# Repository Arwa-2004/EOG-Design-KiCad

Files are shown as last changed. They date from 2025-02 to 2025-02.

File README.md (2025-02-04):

# EOG-Design-KiCad

## Table of Contents
1. [Introduction](#introduction)
2. [Components](#components)
   - [Protection Circuit](#protection-circuit)
   - [Boost Converter](#boost-converter)
   - [5V to -5V Inverting Converter](#5v-to--5v-inverting-converter)
   - [5V to 3.3V Regulator](#5v-to-33v-regulator)
   - [Li-ion Battery Charger](#li-ion-battery-charger)
   - [EOG Filters](#eog-filters)
   - [Flash Memory, UART, and Screen](#flash-memory-uart-and-screen)
   - [ESP32-WROOM-32E](#esp32-wroom-32e)
3. [PCB Design](#pcb-design)
4. [Future Work](#future-work)
5. [Copyright](#Copyright)

## Introduction
EOG (Electrooculography) is used in medical diagnostics to assess eye health and track issues related to the retina and cornea, it is handheld as electrodes are attached. The purpose of my project is to captures eye movement signals using EOG electrodes, processes the data with an ESP32 microcontroller, and displays the results on a screen.



## Components



### Protection Circuit
Is used to ensure that the system is safe from electrical surges. I used 2A fuse to protect against short circuits and overcurrent, a reverse polarity Schottky Diode, as its name suggests it protects the circuit from damage if the power supply is connected with reverse polarity, and a TVS diode SMAJ5.0A which protects sensitive components such as ESP32 from voltage spikes.

### Boost Converter
Which boosts the voltage from +3.6V to +5V, in this case I chose TPS61252DSG. The +5V rail is used to power the filters of EOG signal.

### 5V to -5V inverting converter
I used LM2776 to provide negative -5V supply to the EOG filters.

### 5V to 3.3V regulator 
Steps down the 5V supply to 3.3V for components like the ESP32, which require a 3.3V supply.

### Li-ion Battery Charger
Which charges a single-cell Li-ion battery (3.6V–4.2V) from a 5V input like USB or external adapter.
Charger IC LTC4001EUF#PBF manages the charging process, including constant current (CC) and constant voltage (CV) phases. Moreover, protects the battery from overcharging, over-discharging, and short circuits. Example of bettery used: https://tr.farnell.com/jauch/li18650jc-26-1s1p/batt-rechargeable-li-ion-2-6ah/dp/4551054



### EOG filters
As shown in the picture, I added a 3 pin connector for the electrodes (CH- and CH+) thrid one connected to ground which is behind the ear (in the bony area) as a reference https://store.upsidedownlabs.tech/product/bioamp-cable-v2/. I used instrumentation amplifier to amplify small differential signals from EOG electrodes while rejecting common-mode noise like interference from power lines 50Hz or 60Hz,or other sources.
The INA333xxDGK has a precise gain that can be set using a single external resistor, a high CMRR, and a low noise. 
I added user safety composed of TVS diodes to safeguard the user and the equipment from voltage spikes, electrostatic discharge (ESD), or reverse polarity.

Then, I connected IA to a high pass filter of 0.053Hz to process the amplified signal and remove unwanted DC low-frequency components, ensuring that only the relevant EOG signals (related to eye movements) are processed, which is connected to 50Hz notch filter to remove power line interference of 50Hz that is connected to class 1 and 2 of low pass filter, 1st class low pass filter 23.42Hz, is used to remove high-frequency noise and ensure that only the relevant EOG signals (typically in the range of 0.1 Hz to 30 Hz) are preserved. Furthermore, integrating 2nd class low-pass filter, 19.42Hz to effectively attenuates frequencies above the cutoff frequency (19.42 Hz), ensuring that high-frequency noise is removed more aggressively, which is conncted to the ESP32.

### Flash Memory, UART, and Screen
The OLED screen (AOM12864A0-1.54WW-ANO) to show EOG signals, eye movement patterns, or system parameters. The flash memory to store EOG signals for later analysis. Finally, UART to send EOG data to a computer for analysis. Note: this EOG is designed to retrieve or analyze the stored data later as needed as I'll depend on bluetooth build inside esp32 (coding) for data transfer. a BluetoothSerial used to communicate with a Bluetooth terminal app or custom software. In short I wont need a USB.



### ESP32-WROOM-32E
Is the brain of the system, since ESP32 enables communication between the EOG system and external devices,  processes the EOG signals captured by the electrodes and amplified/filtered by the analog front-end filters, displays real-time EOG data or system status on an OLED screen, and stores EOG data in flash memory or an external SD card for later analysis.



## PCB design
I used 4 layers (signal/ gnd/ power/ signal), I made sure that sensitive analog ciruits of the filters are far away from the noisy digital parts such as esp32, and I put decoupling capacitor 100 nF close to the power pins of each IC (ESP32, INA333xxDGK, filters, etc..)





## Future Work
This project is designed to retrieve and analyze stored EOG data as needed. Future improvements and planned features include:

1. **Bluetooth Data Transfer:**
   - The ESP32's built-in Bluetooth capability will be used for wireless data transfer, eliminating the need for a USB connection.
2. **Optimized Signal Processing:**
   - Further refinement of the EOG signal filters to improve noise immunity and signal accuracy.
   - Implementation of advanced signal processing algorithms (e.g., wavelet transforms) for better eye movement detection.

3. **Wireless Charging:**
   - Integration of a wireless charging module to enhance the portability and usability of the device.

4. **Mobile App Integration:**
   - Development of a mobile app to visualize EOG data in real-time and provide diagnostic insights.

## Copyright
Copyright (c) 2025 Arwa Basal
All rights reserved.

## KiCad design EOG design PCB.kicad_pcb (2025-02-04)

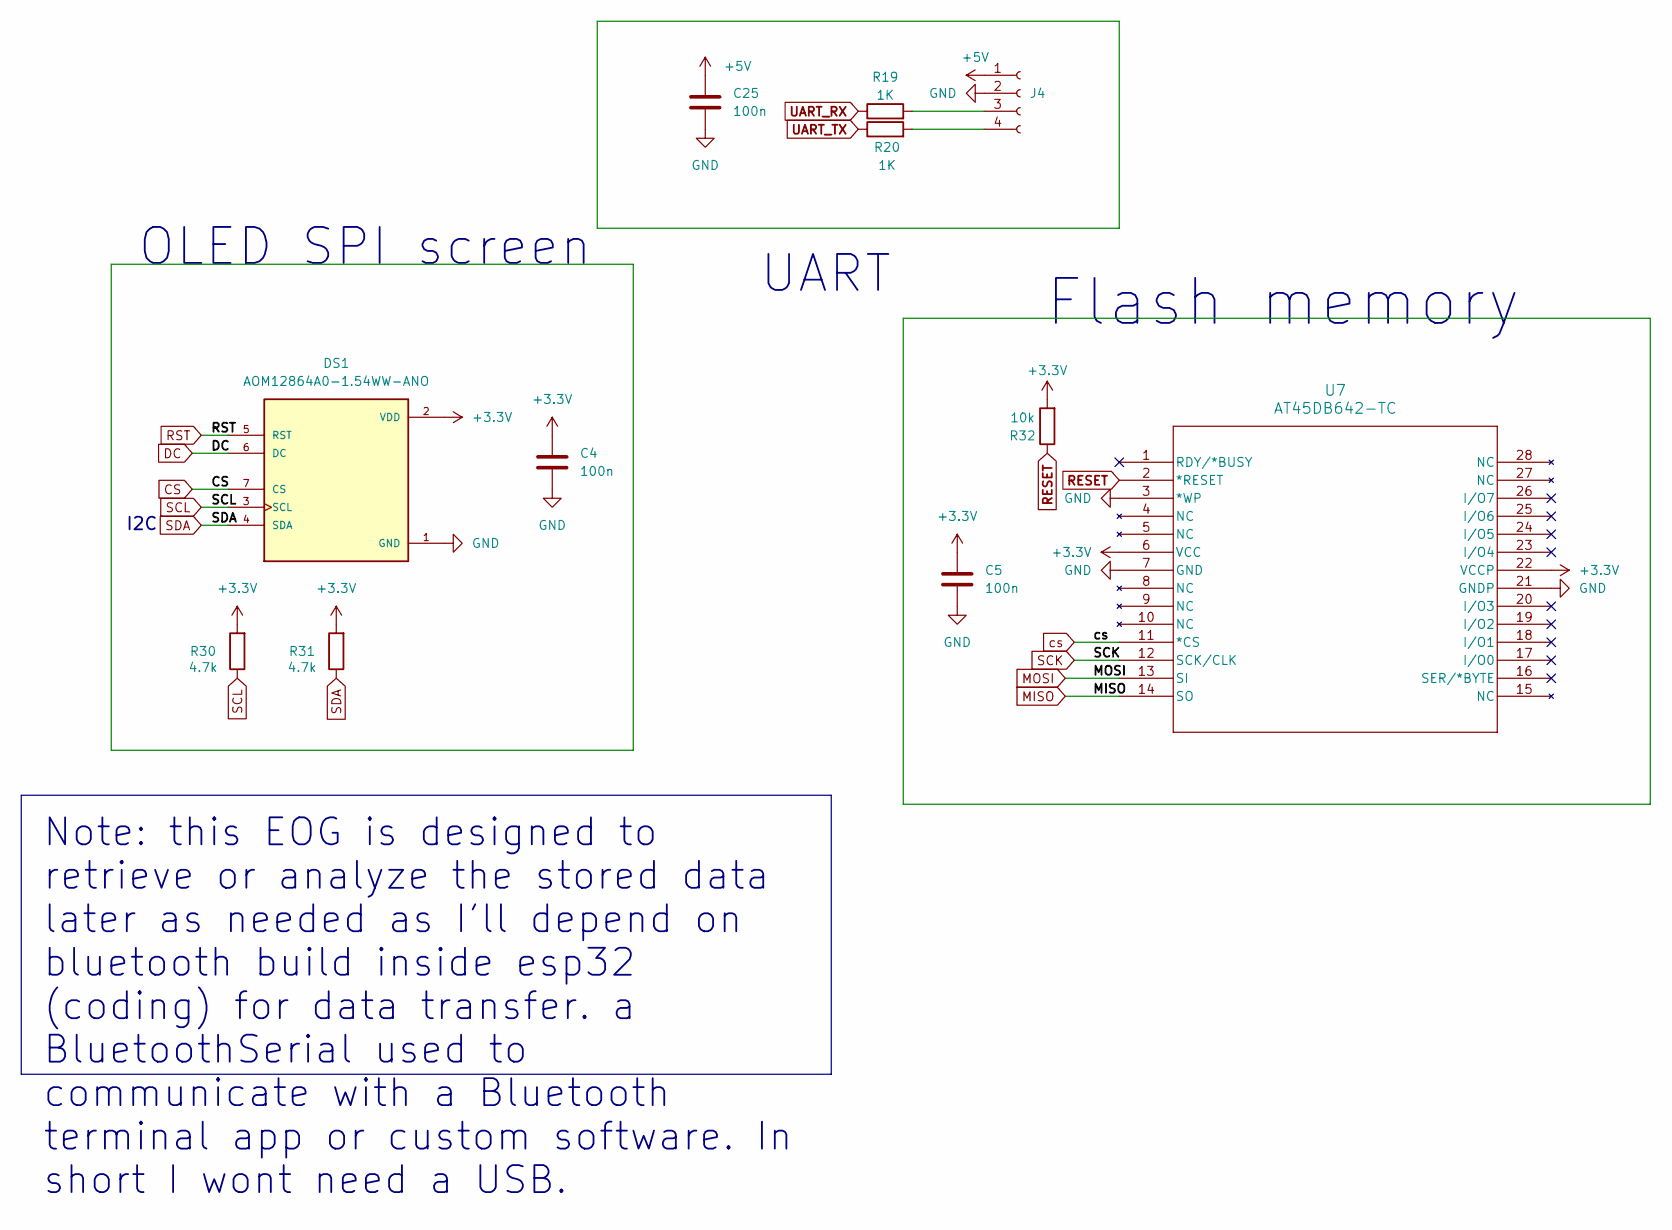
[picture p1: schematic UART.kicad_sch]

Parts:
C4, C5, C25: 100n; C_0603_1608Metric
DS1: AOM12864A0-1.54WW-ANO; LCD_AOM12864A0-1.54WW-ANO; PARTREV O; DigiKey_Part_Number 5491-AOM12864A0-1.54WW-ANO-ND
J4: Conn_01x04_Socket; PinHeader_2x02_P1.00mm_Vertical
R19, R20: 1K; R_0603_1608Metric
R30, R31: 4.7k; R_0603_1608Metric
R32: 10k; R_0603_1608Metric
U7: AT45DB642-TC; TSOP28_8x11P8_MCH

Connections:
+3.3V: C4.1, C5.1, DS1.2 (VDD), R30.2, R31.2, R32.2, U7.6 (VCC), U7.22 (VCCP); also elsewhere on the board
+5V: C25.1, J4.1; also elsewhere on the board
CS: DS1.7 (CS); also elsewhere on the board
DC: DS1.6 (DC); also elsewhere on the board
GND: C4.2, C5.2, C25.2, DS1.1 (GND), J4.2, U7.3 (*WP), U7.7 (GND), U7.21 (GNDP); also elsewhere on the board
MISO: U7.14 (SO); also elsewhere on the board
MOSI: U7.13 (SI); also elsewhere on the board
unnamed: J4.3, R19.2
unnamed: J4.4, R20.2
RESET: R32.1, U7.2 (*RESET)
RST: DS1.5 (RST); also elsewhere on the board
SCK: U7.12 (SCK/CLK); also elsewhere on the board
SCL: DS1.3 (SCL), R30.1; also elsewhere on the board
SDA: DS1.4 (SDA), R31.1; also elsewhere on the board
UART_RX: R19.1; also elsewhere on the board
UART_TX: R20.1; also elsewhere on the board
cs: U7.11 (*CS); also elsewhere on the board

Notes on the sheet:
Note: this EOG is designed to retrieve or analyze the stored data later as needed as I'll depend on bluetooth build inside esp32 (coding) for data transfer. a BluetoothSerial used to communicate with a Bluetooth terminal app or custom software. In short I wont need a USB.
OLED SPI screen
I2C
UART
Flash memory

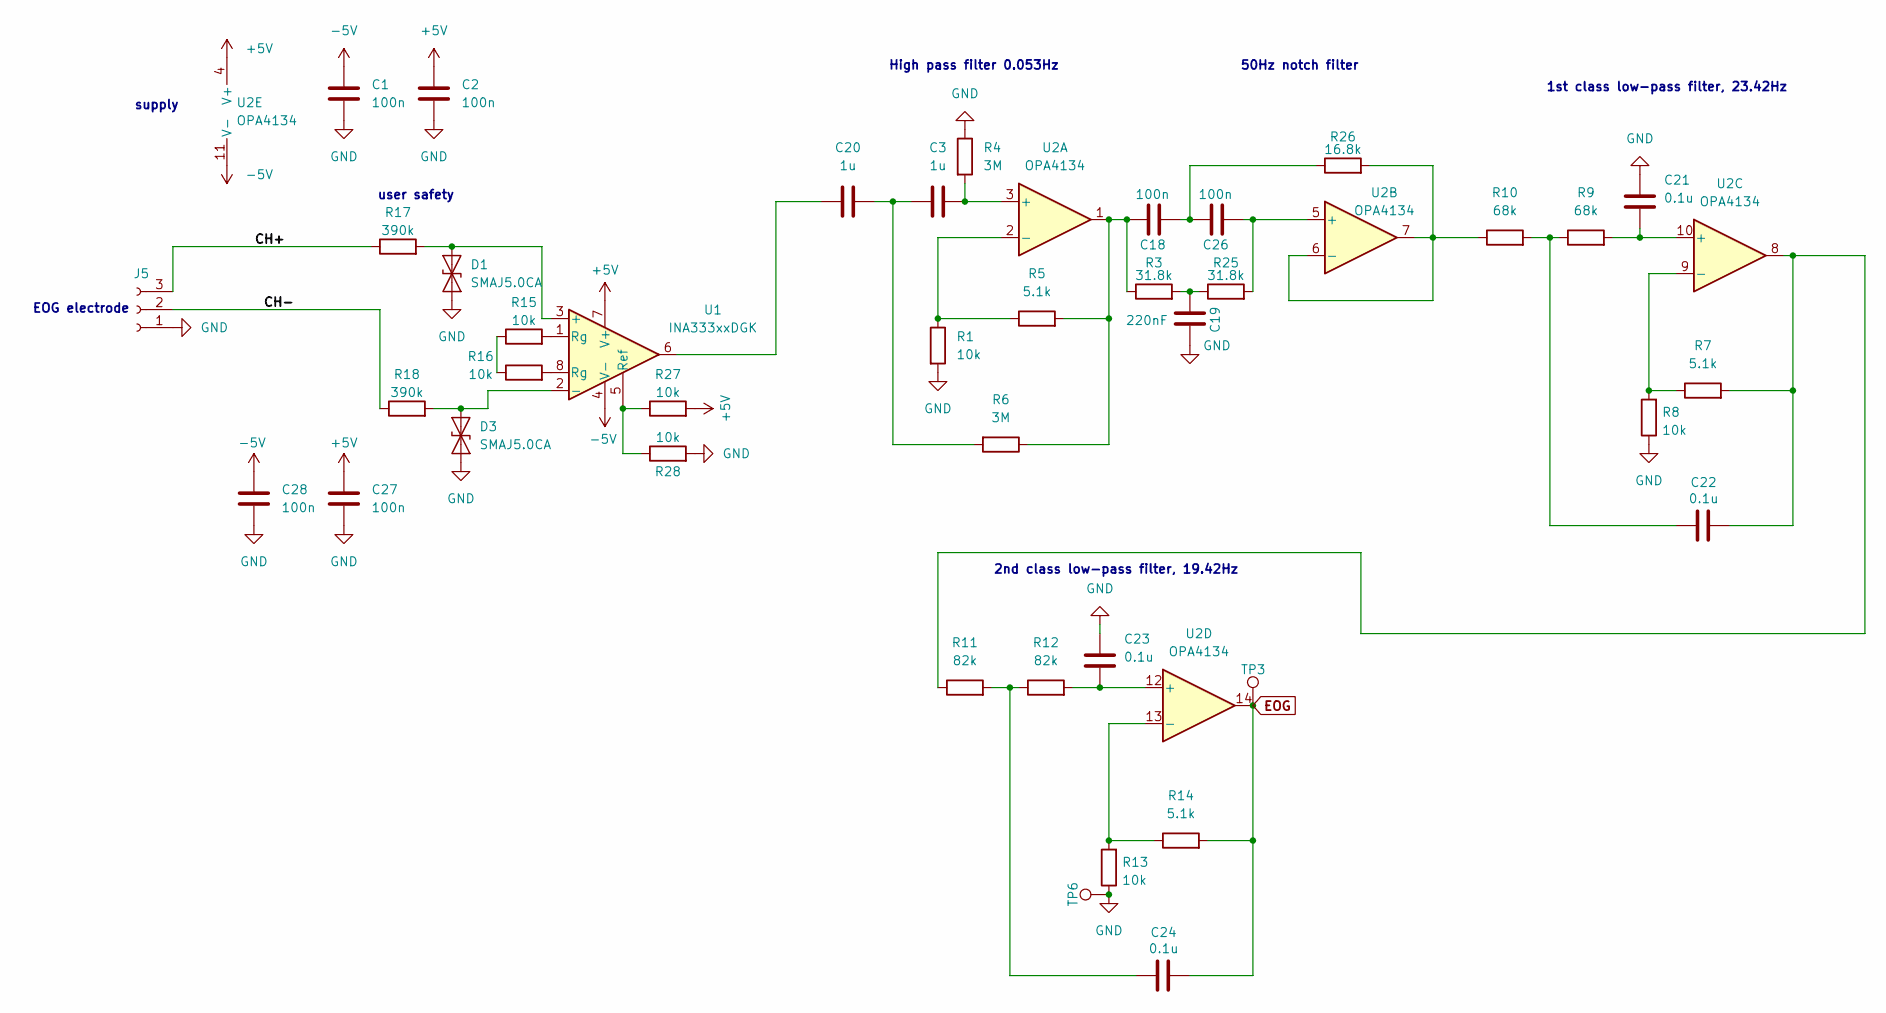
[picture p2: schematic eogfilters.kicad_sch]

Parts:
C1, C2, C18, C26, C27, C28: 100n; C_0603_1608Metric
C3, C20: 1u; C_0603_1608Metric
C19: 220nF; C_0603_1608Metric
C21, C22, C23, C24: 0.1u; C_0603_1608Metric
D1, D3: SMAJ5.0CA; D_SMA
J5: Conn_01x03_Socket; JST_PH_B3B-PH-K_1x03_P2.00mm_Vertical
R1, R8, R13, R15, R16, R27, R28: 10k; R_0603_1608Metric
R3, R25: 31.8k; R_0603_1608Metric
R4, R6: 3M; R_0603_1608Metric
R5: 5.1k; C_0805_2012Metric
R7, R14: 5.1k; R_0805_2012Metric
R9, R10: 68k; R_0603_1608Metric
R11, R12: 82k; R_0603_1608Metric
R17, R18: 390k; R_0603_1608Metric
R26: 16.8k; RES_SMR3DZ_VIS
TP3, TP6: TestPoint; TestPoint_Pad_D1.5mm
U1: INA333xxDGK; VSSOP-8_3x3mm_P0.65mm
U2: OPA4134; SOIC127P600X175-14N

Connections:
+5V: C2.1, C27.1, R27.2, U1.7 (V+), U2.4 (V+); also elsewhere on the board
-5V: C1.1, C28.1, U1.4 (V-), U2.11 (V-); also elsewhere on the board
/Filters/CH+: J5.3, R17.1
/Filters/CH-: J5.2, R18.1
EOG: C24.1, R14.2, TP3.1, U2.14; also elsewhere on the board
GND: C1.2, C2.2, C19.1, C21.2, C23.2, C27.2, C28.2, D1.1 (A1), D3.1 (A1), J5.1, R1.2, R4.1, R8.1, R13.1, R28.2, TP6.1; also elsewhere on the board
unnamed: C18.1, R3.1, R5.2, R6.1, U2.1
unnamed: C18.2, C26.1, R26.1
unnamed: C19.2, R3.2, R25.1
unnamed: C20.1, U1.6
unnamed: C3.1, C20.2, R6.2
unnamed: C22.1, R7.2, R11.1, U2.8
unnamed: C22.2, R9.1, R10.2
unnamed: C24.2, R11.2, R12.1
unnamed: D1.2 (A2), R17.2, U1.3 (+)
unnamed: D3.2 (A2), R18.2, U1.2 (-)
unnamed: R15.1, R16.1
unnamed: R15.2, U1.1 (Rg)
unnamed: R16.2, U1.8 (Rg)
unnamed: R27.1, R28.1, U1.5 (Ref)
unnamed: C3.2, R4.2, U2.3 (+)
unnamed: R1.1, R5.1, U2.2 (-)
unnamed: C26.2, R25.2, U2.5 (+)
unnamed: R10.1, R26.2, U2.6 (-), U2.7
unnamed: C21.1, R9.2, U2.10 (+)
unnamed: R7.1, R8.2, U2.9 (-)
unnamed: C23.1, R12.2, U2.12 (+)
unnamed: R13.2, R14.1, U2.13 (-)

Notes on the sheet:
supply
2nd class low-pass filter, 19.42Hz
50Hz notch filter
user safety
High pass filter 0.053Hz
EOG electrode
1st class low-pass filter, 23.42Hz

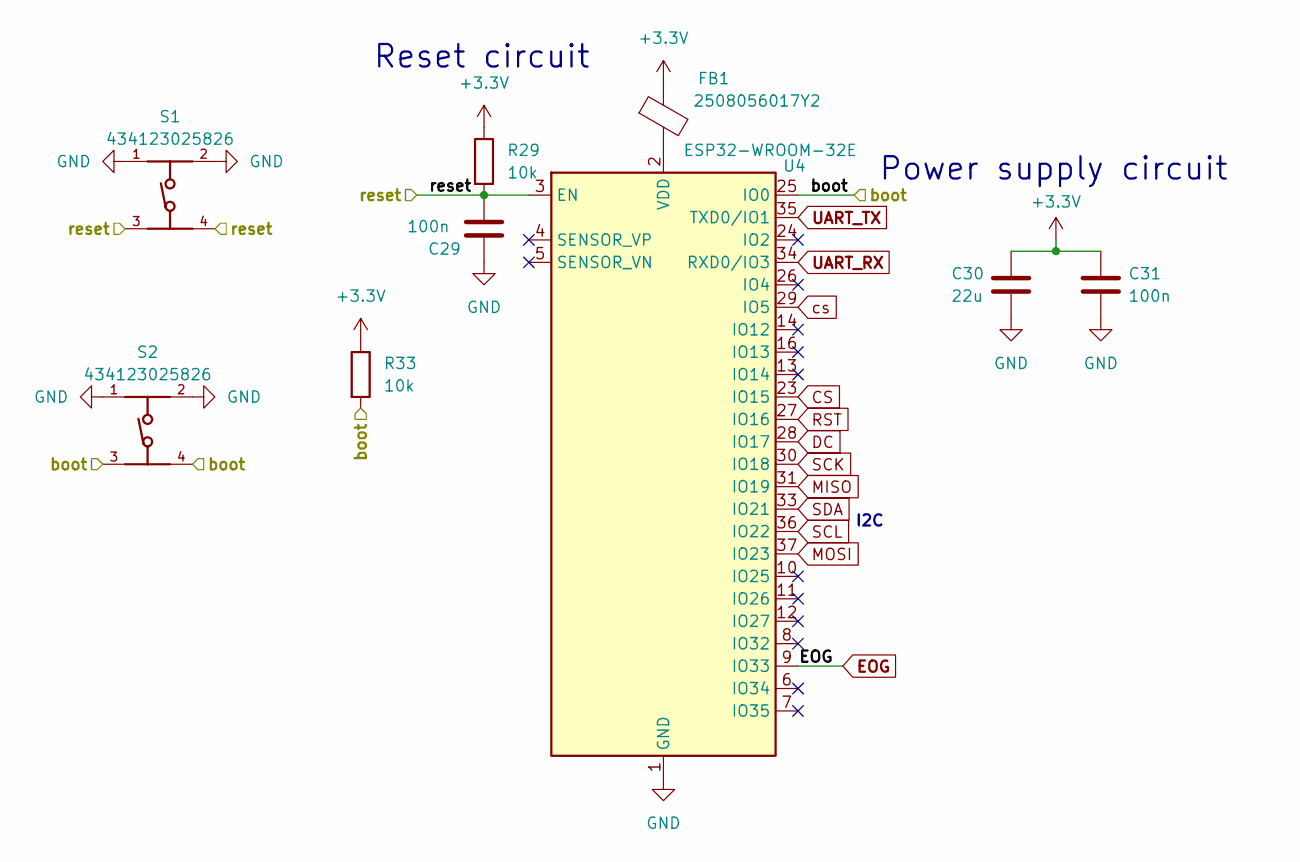
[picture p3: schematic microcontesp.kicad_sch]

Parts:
C29, C31: 100n; C_0603_1608Metric
C30: 22u; C_0805_2012Metric
FB1: 2508056017Y2; IND_25_0805_FRT
R29, R33: 10k; R_0603_1608Metric
S1, S2: 434123025826; PART-NUMBER 434123025826
U4: ESP32-WROOM-32E; ESP32-WROOM-32D

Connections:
+3.3V: C30.1, C31.1, FB1.1, R29.1, R33.1; also elsewhere on the board
/ESP32-WROOM-32E/boot: R33.2, S2.3, S2.4, U4.25 (IO0)
/ESP32-WROOM-32E/reset: C29.2, R29.2, S1.3, S1.4, U4.3 (EN)
CS: U4.23 (IO15); also elsewhere on the board
DC: U4.28 (IO17); also elsewhere on the board
EOG: U4.9 (IO33); also elsewhere on the board
GND: C29.1, C30.2, C31.2, S1.1, S1.2, S2.1, S2.2, U4.1 (GND), U4.15 (GND), U4.38 (GND), U4.39 (GND); also elsewhere on the board
MISO: U4.31 (IO19); also elsewhere on the board
MOSI: U4.37 (IO23); also elsewhere on the board
unnamed: FB1.2, U4.2 (VDD)
RST: U4.27 (IO16); also elsewhere on the board
SCK: U4.30 (IO18); also elsewhere on the board
SCL: U4.36 (IO22); also elsewhere on the board
SDA: U4.33 (IO21); also elsewhere on the board
UART_RX: U4.34 (RXD0/IO3); also elsewhere on the board
UART_TX: U4.35 (TXD0/IO1); also elsewhere on the board
cs: U4.29 (IO5); also elsewhere on the board

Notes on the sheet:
Reset circuit
Power supply circuit
I2C

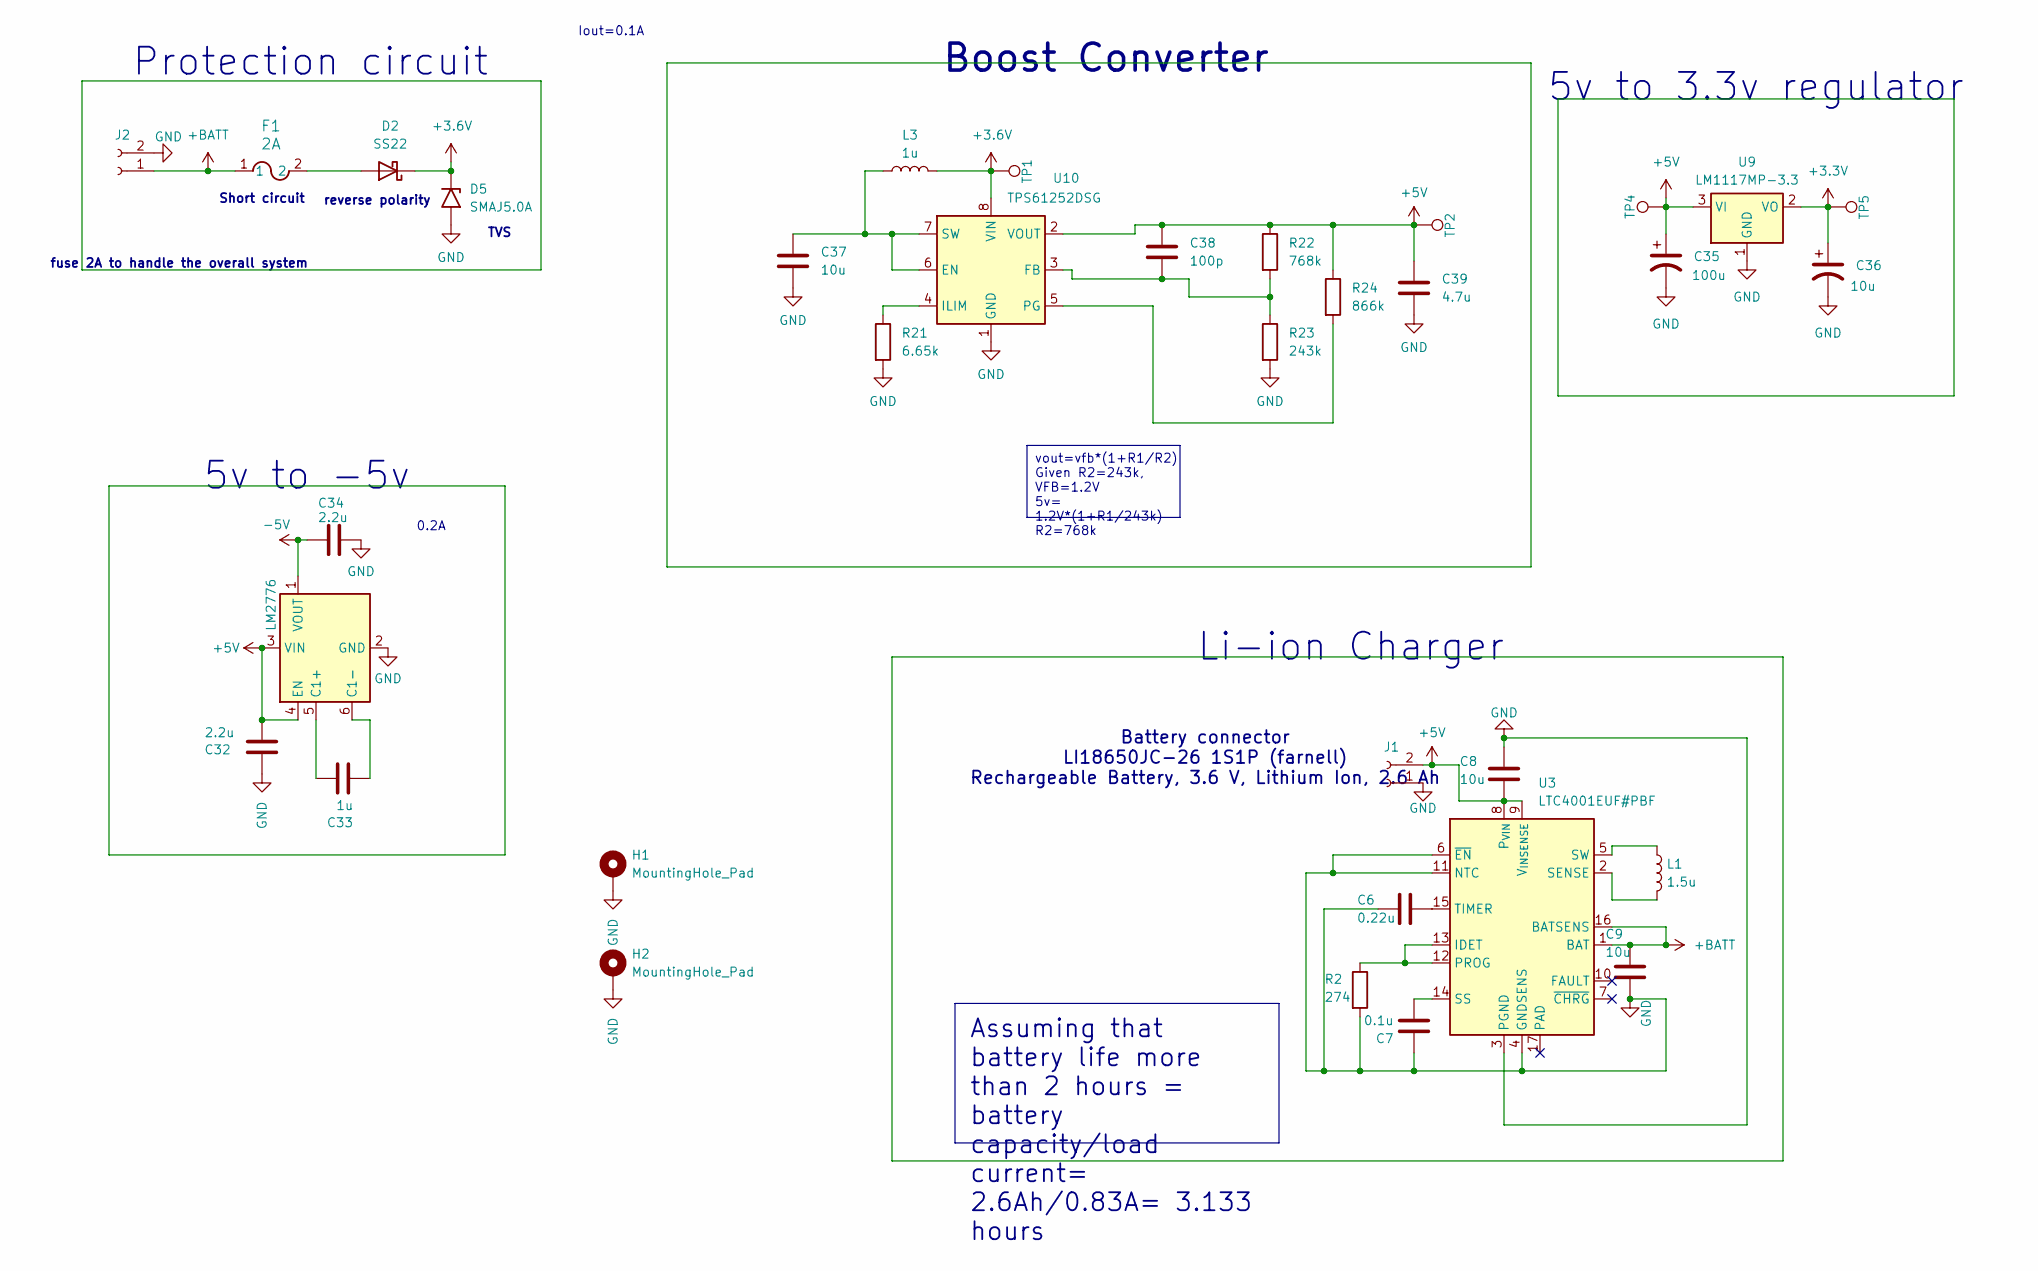
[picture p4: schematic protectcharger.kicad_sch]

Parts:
C6: 0.22u; C_0603_1608Metric
C7: 0.1u; C_0603_1608Metric
C8, C9: 10u; C_0805_2012Metric
C32, C34: 2.2u; C_0603_1608Metric
C33: 1u; C_0603_1608Metric
C35: 100u; WCAP-ATG8_5X11_DXL_
C36: 10u; WCAP-ATG8_5X11_DXL_
C37: 10u; C_0603_1608Metric
C38: 100p; C_0603_1608Metric
C39: 4.7u; C_0402_1005Metric
D2: SS22; D_SMA
D5: SMAJ5.0A; D_SMA
F1: 2A; Fuse_0603_1608Metric
H1, H2: MountingHole_Pad; MountingHole_3.2mm_M3_Pad
J1: LI18650JC-26 1S1P (farnell); JST_XA_B02B-XASK-1_1x02_P2.50mm_Vertical
J2: Conn_01x02_Socket; JST_XA_B02B-XASK-1_1x02_P2.50mm_Vertical
L1: 1.5u; INDC2016X100N
L3: 1u; INDC2016X100N
R2: 274; R_0805_2012Metric
R21: 6.65k; R_0402_1005Metric
R22: 768k; R_0402_1005Metric
R23: 243k; R_0402_1005Metric
R24: 866k; R_0201_0603Metric
TP1, TP2, TP4, TP5: TestPoint; TestPoint_Pad_D1.5mm
U3: LTC4001EUF#PBF; QFN-16-1EP_4x4mm_P0.65mm_EP2.15x2.15mm
U8: LM2776; SOT-23-6
U9: LM1117MP-3.3; SOT-223-3_TabPin2
U10: TPS61252DSG; WSON-8-1EP_2x2mm_P0.5mm_EP0.9x1.6mm

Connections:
+3.3V: C36.1, TP5.1, U9.2 (VO); also elsewhere on the board
+3.6V: D2.1 (K), D5.1 (A1), L3.2, TP1.1, U10.8 (VIN)
+5V: C8.2, C32.2, C35.1, C38.1, C39.1, J1.2, R22.1, R24.1, TP2.1, TP4.1, U3.8 (P_{VIN}), U3.9 (V_{INSENSE}), U8.3 (VIN), U8.4 (EN), U9.3 (VI), U10.2 (VOUT); also elsewhere on the board
+BATT: C9.1, F1.1, J2.1, U3.1 (BAT), U3.16 (BATSENS)
-5V: C34.1, U8.1 (VOUT); also elsewhere on the board
GND: C6.2, C7.1, C8.1, C9.2, C32.1, C34.2, C35.2, C36.2, C37.2, C39.2, D5.2 (A2), H1.1, H2.1, J1.1, J2.2, R2.2, R21.2, R23.2, U3.3 (PGND), U3.4 (GNDSENS), U3.6 (~EN), U3.11 (NTC), U8.2 (GND), U9.1 (GND), U10.1 (GND), U10.9 (GND); also elsewhere on the board
unnamed: D2.2 (A), F1.2
unnamed: R2.1, U3.12 (PROG), U3.13 (IDET)
unnamed: L1.2, U3.2 (SENSE)
unnamed: C7.2, U3.14 (SS)
unnamed: L1.1, U3.5 (SW)
unnamed: C6.1, U3.15 (TIMER)
unnamed: C33.1, U8.5 (C1+)
unnamed: C33.2, U8.6 (C1-)
unnamed: C37.1, L3.1, U10.6 (EN), U10.7 (SW)
unnamed: C38.2, R22.2, R23.1, U10.3 (FB)
unnamed: R21.1, U10.4 (ILIM)
unnamed: R24.2, U10.5 (PG)

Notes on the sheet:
vout=vfb*(1+R1/R2) Given R2=243k, VFB=1.2V 5v= 1.2V*(1+R1/243k) R2=768k
Assuming that battery life more than 2 hours = battery capacity/load current= 2.6Ah/0.83A= 3.133 hours
5v to -5v
reverse polarity
Short circuit
Iout=0.1A
0.2A
fuse 2A to handle the overall system
Protection circuit
Boost Converter
Battery connector LI18650JC-26 1S1P (farnell) Rechargeable Battery, 3.6 V, Lithium Ion, 2.6 Ah
Li-ion Charger
5v to 3.3v regulator
TVS

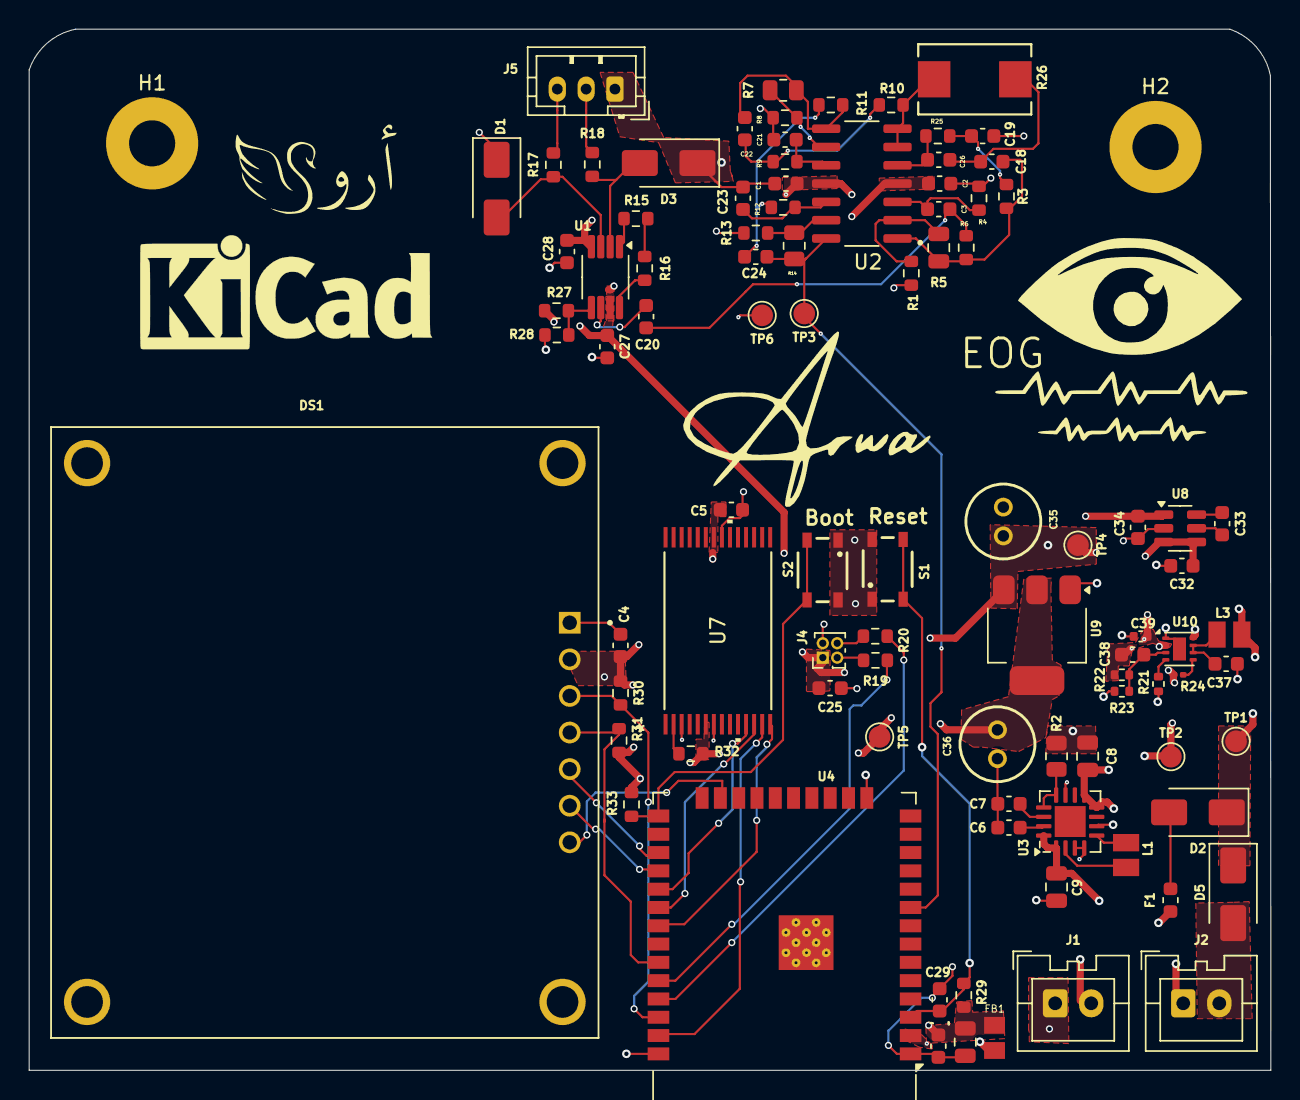
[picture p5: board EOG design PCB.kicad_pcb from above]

Board: 4 copper layers, 86.2 x 72.3 mm, 95 parts (0 on the bottom side), 60 nets.
